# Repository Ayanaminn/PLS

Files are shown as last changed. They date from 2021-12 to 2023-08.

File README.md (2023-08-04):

# PLS (Zebrafish Embryo Photomotor Response and Larval Predator response system)
PLS (Zebrafish Embryo Photomotor Response and Larval Predator response system) is developed for rapid analysis of large cohorts of specimens in PMR and SPR neurotoxicity bioassays. 

PLS includes applications of custom embryo arrays in conjunction with an open-source and inexpensive infrared video imaging system coupled with a dedicated bioinformatic approach that facilitates high-throughput analysis of behavioural phenotypes.

PLS_overview

The photic stimulus is controlled by PMR Control Panel, a custom software application that enables programmable photic stimulus control through interfacing with Arduino-based microcontroller.



**Please cite our manuscript:**

Henry, J., Bai, Y., Kreuder, F., Mawdsley, D., Kaslin, J., & Wlodkowic, D. (2022). Accelerating Chemobehavioral Phenotypic Screening in Neurotoxicology Using a Living Embryo Array System. Zebrafish, 19(1), 32-35. https://doi.org/10.1089/zeb.2021.0072 

Installation:
------------
### Requirements

* Windows operating system.

* [Key Componect List](https://github.com/Ayanaminn/PLS/blob/master/Hardware/Assembley%20Instructions%20and%20Component%20List.docx).

### Software

1. Download the latest release from [Releases](https://github.com/Ayanaminn/PLS/releases).

2. Unzip file and open "PMR control panel" folder.

3. Double click to run "PMR control panel.exe".

### Hardware

1. Following the [Assembly instructions](https://github.com/Ayanaminn/PLS/blob/master/Hardware/Assembley%20Instructions%20and%20Component%20List.docx).

2. Download the latest release from [Releases](https://github.com/Ayanaminn/PLS/releases).

3. Unzip file and open "PMR control panel Arduino script" folder.

4. Using [Arduino IDE](https://www.arduino.cc/en/software) to open the "PMR_control_panel_Arduino_script.ino" and upload it to board.

5. Wire LED circuit to Arduino pin 9 (default pin), if user prefer to use other pins, change pin number in the script accordingly and re-upload.

Getting Started:
------------

1. Connect the Arduino with the computer.

2. In the PMR control panel, select the Arduino port, then click "Connect".

3. Use manual or auto mode to control light stimulus.

4. Disconnect the Arduino before exit the program.

License:
------------

MIT License. See [LICENSE](https://github.com/Ayanaminn/PLS/blob/master/LICENSE) for details.

Contact:
------------

Should you have any questions about this application, please report an issue [here](https://github.com/Ayanaminn/PLS/issues), or send an [email](mailto:yutao.bai@hotmail.com).

If you have further interests about the research this program has been applied for, please [visit our website](https://neurotoxlab.com).

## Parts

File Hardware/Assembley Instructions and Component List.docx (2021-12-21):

Key Component List

- 1x Arduino board. Arduino Uno was validated, however any USB interfacing board that has digital I/O pins with PWM should work.
- 1x BD135 transistor.
- 2x 12V CREE LEDs (High intensity to stimulate PMR).
- 1x Power pack for CREE LEDs (AA-0594), input 9-30V, output 700mA.
- 12x 3 strip flexible 12V adhesive white LEDs (ZD0577) for LPR stimulus lighting (36 total LEDs).
- 1x ZS-X4B Hardwired PWM, with 3-15V circuit soldered to allow to run on 12V.
- 1x flexible 12V adhesive IR (850nm) LEDs (LM3528-WN60) for orthogonal IR lighting (24 total LEDs).
- 1x Micro camera stand for CREE LEDs.
- 1x Standard 12V power supply.
- 1x Laser cut PMMA construction base as per below assembly instructions.

Assembly instructions

1. Laser cut all PMMA components. The design for all components that were laser cut are included as .dxf files. These files are already scaled and should be usable by any laser cutter. Always ensure the laser cutter control program correctly imports the layout and the colour should be changed depending on specific cutting settings for thickness of PMMA. Ensure standard safe operating procedure of the laser cutter.
2. Edge components for the base construction need to be layered and thermally bonded as follows, from inside to out, 2x 1.5mm long, 4.5mm long, 4.5mm outer long and 2x 1.5mm short, 4.5mm short, 4.5mm outer short. The thermal bonding method is described in the supplementary.
3. Once these are bonded every piece will slot together with the base to form the overall construction – this can then be chemically bonded.
4. Included in the .dxf files are the custom plate designs. These are simple two layer thermally bonded constructions, the top layer with the holes and the bottom layer with a standard rectangle.
5. Included in the .dxf files are CREE LED brackets for connection to the micro stand, these will have to be altered depending on the stand.
6. The orthogonal IR LEDs can be adhered to the upper edge (4.5mm outer PMMA layer) of the base construction, ensuring the centre of the LEDs align with the centre of the embryo plate when located.
7. The 12 LPR 3 strip LED sections can be wired together and adhered to the baseplate of the base construction, ensure the wiring exits via one of the allocated holes in the edge design.
8. The orthogonal IR LEDs are to be wired into the hardwired PWM (to allow dimming in the background lighting) and the PWM connected to the 12V power supply.
9. The Arduino Uno should be wired to provide a 3.3V control signal to the BD135 transistor (acts as a switch). The BD 135 transistor is connected in a standard simple transistor circuit with the 12V supply that can be wired with removable connections to either the above CREE LEDs (for PMR) or the below white strip LEDs (for LPR).

For further assistance, information or collaboration please contact the Neurotox Lab (https://www.neurotoxlab.com/) at RMIT.

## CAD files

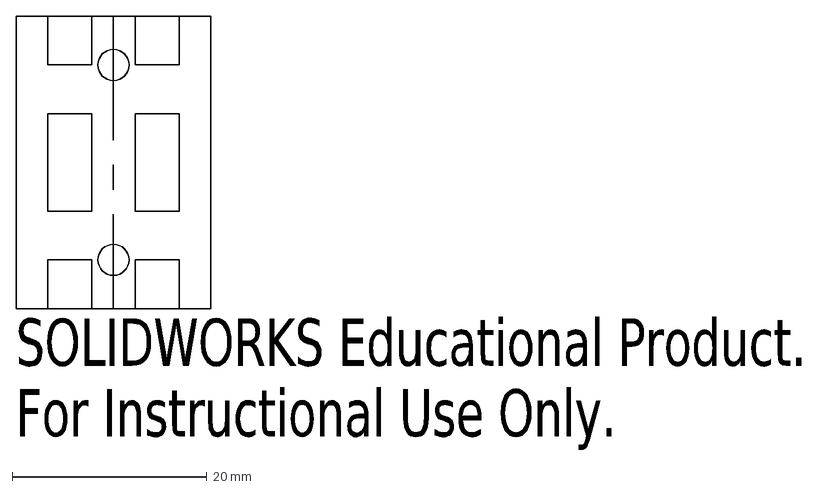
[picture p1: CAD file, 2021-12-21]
Hardware/CREE LED bracket/uprightback_2.DXF
SOLIDWORKS Educational Product.
For Instructional Use Only.

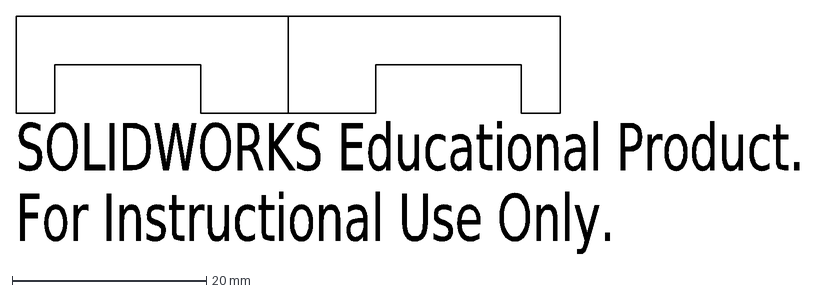
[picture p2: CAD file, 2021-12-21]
Hardware/Main/15short.DXF
SOLIDWORKS Educational Product.
For Instructional Use Only.

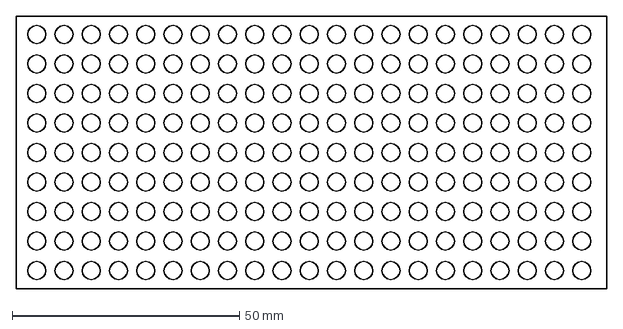
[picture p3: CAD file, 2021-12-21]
Hardware/Plates/zfchip_pmr_plate.DXF
130.0 x 60.0 mm

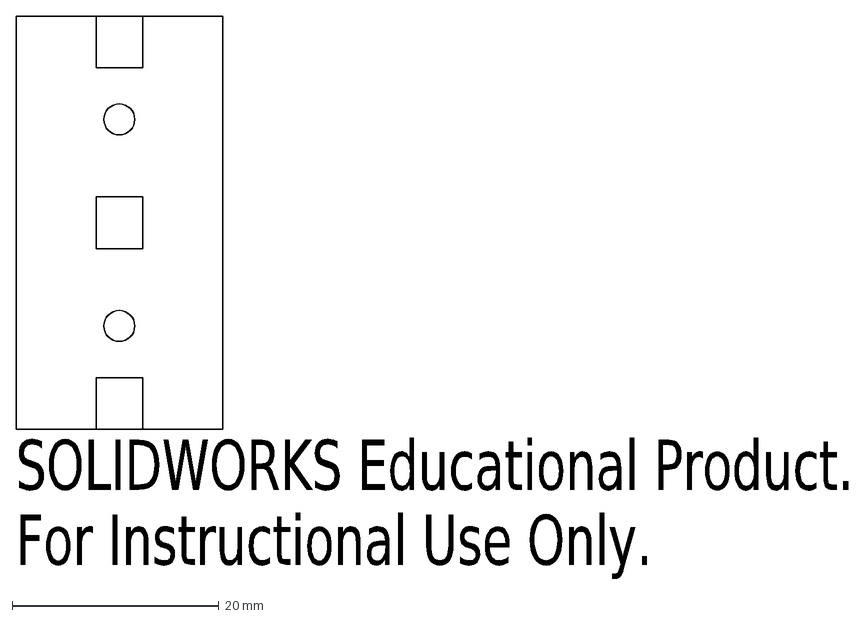
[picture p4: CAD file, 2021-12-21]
Hardware/CREE LED bracket/mountconnection.DXF
SOLIDWORKS Educational Product.
For Instructional Use Only.

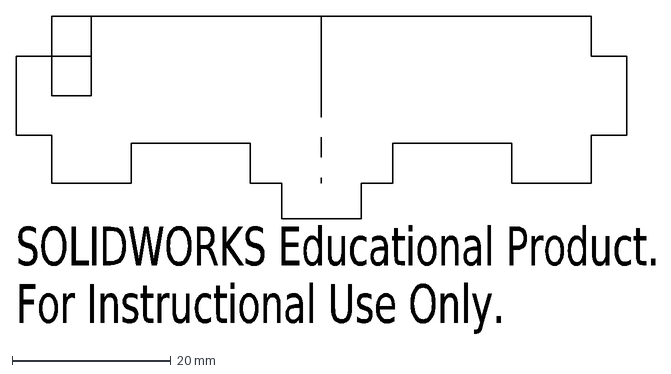
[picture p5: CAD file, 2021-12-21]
Hardware/Main/45outershort.DXF
SOLIDWORKS Educational Product.
For Instructional Use Only.

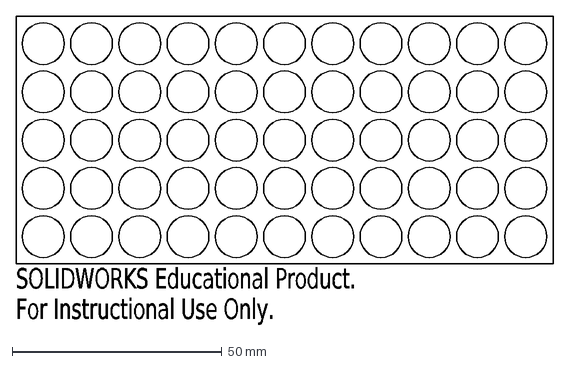
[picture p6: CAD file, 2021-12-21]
Hardware/Plates/zfchip_10mm.DXF
SOLIDWORKS Educational Product.
For Instructional Use Only.

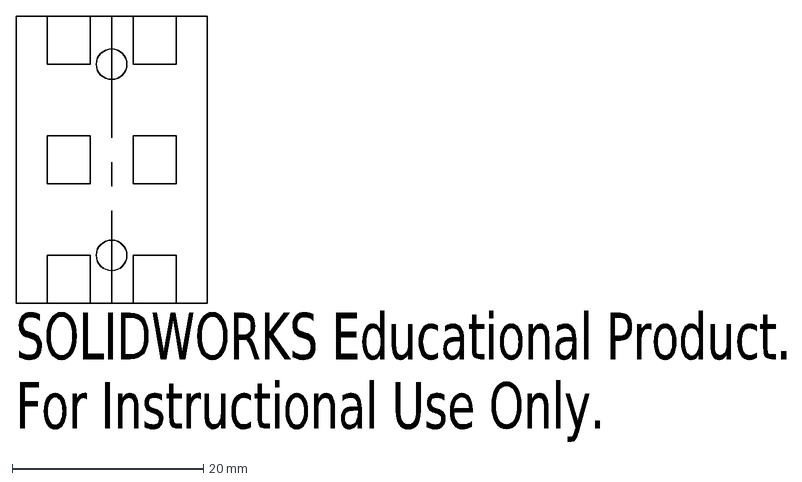
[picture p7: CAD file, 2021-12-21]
Hardware/CREE LED bracket/uprightback.DXF
SOLIDWORKS Educational Product.
For Instructional Use Only.

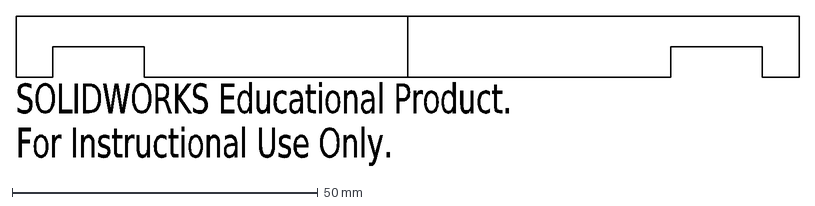
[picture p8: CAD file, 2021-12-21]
Hardware/Main/15long.DXF
SOLIDWORKS Educational Product.
For Instructional Use Only.

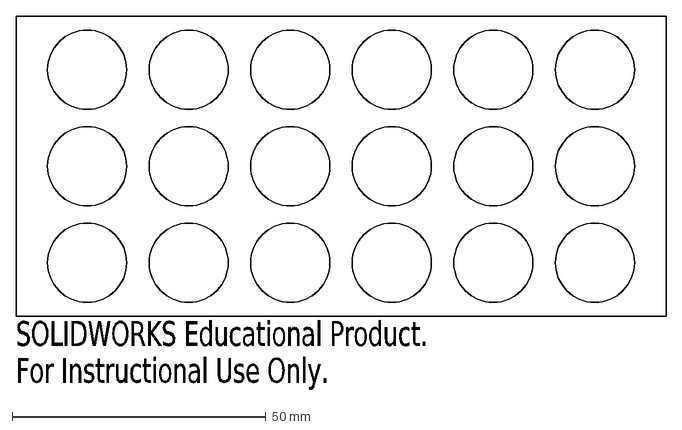
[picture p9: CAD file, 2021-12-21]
Hardware/Plates/zfchip_15dot6mm.DXF
SOLIDWORKS Educational Product.
For Instructional Use Only.

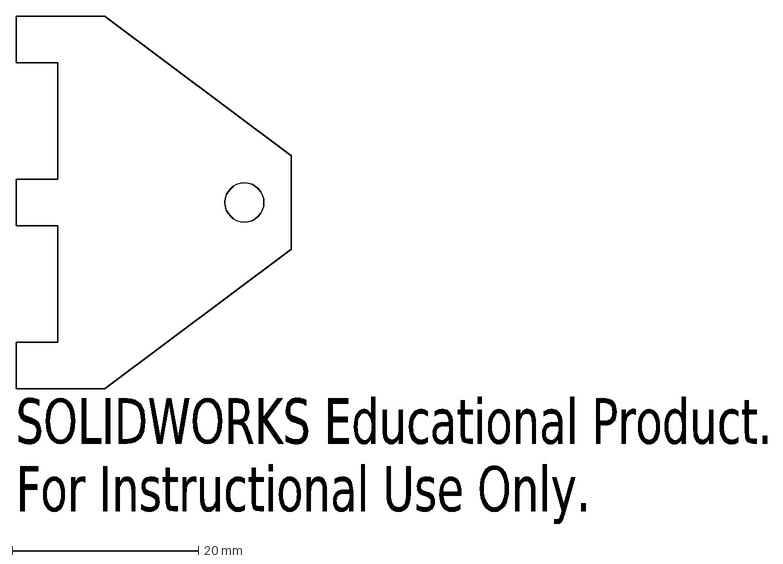
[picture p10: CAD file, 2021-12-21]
Hardware/CREE LED bracket/mountconnecttriangle.DXF
SOLIDWORKS Educational Product.
For Instructional Use Only.

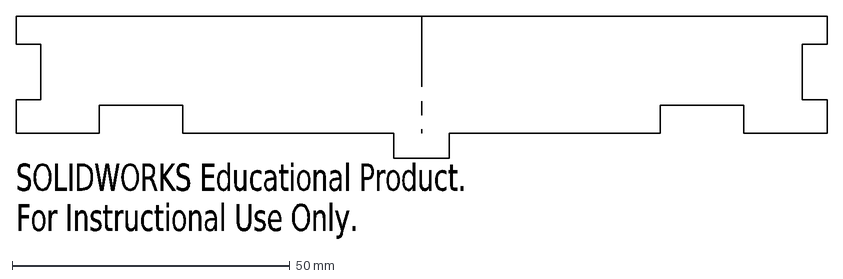
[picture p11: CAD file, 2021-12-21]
Hardware/Main/45outerlong.DXF
SOLIDWORKS Educational Product.
For Instructional Use Only.

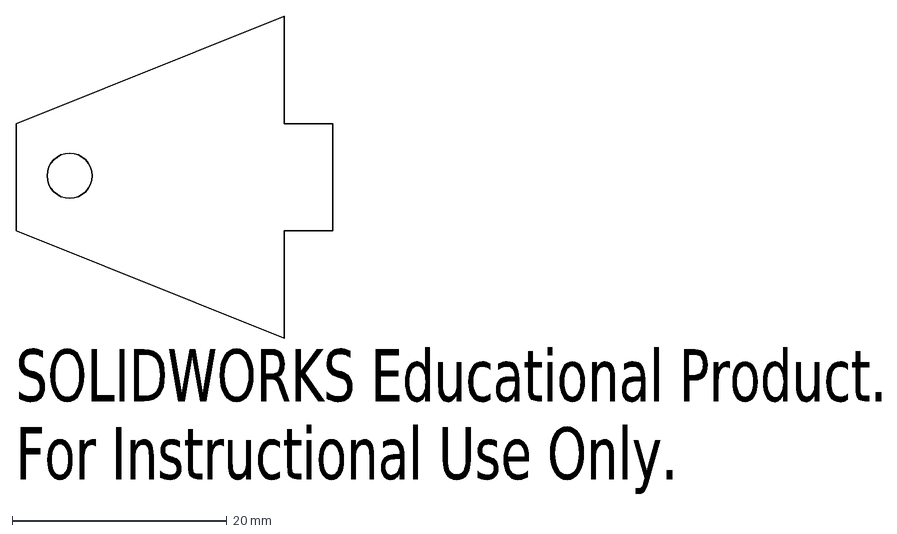
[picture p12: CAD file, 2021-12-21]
Hardware/CREE LED bracket/uprightri_2.DXF
SOLIDWORKS Educational Product.
For Instructional Use Only.

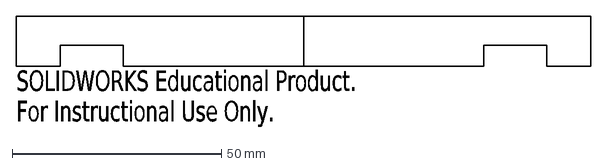
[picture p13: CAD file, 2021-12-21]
Hardware/Main/45long.DXF
SOLIDWORKS Educational Product.
For Instructional Use Only.

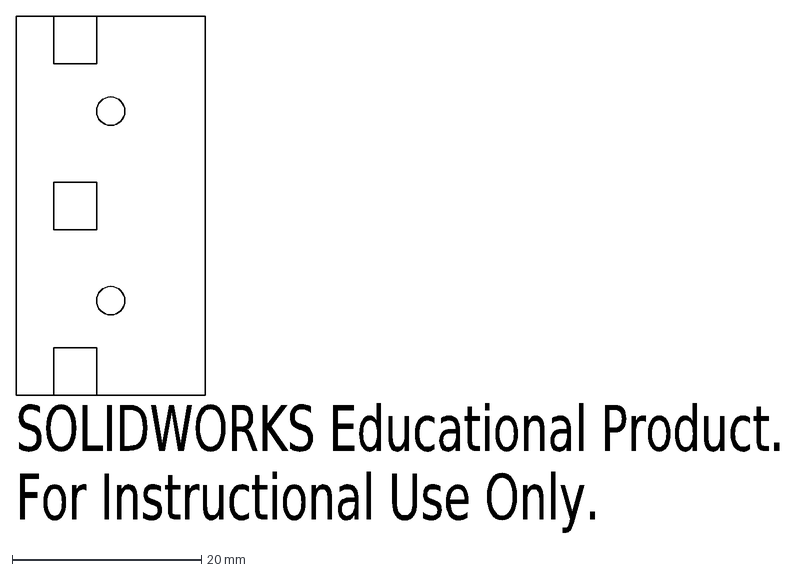
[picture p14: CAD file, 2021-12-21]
Hardware/CREE LED bracket/mountconnection_2.DXF
SOLIDWORKS Educational Product.
For Instructional Use Only.

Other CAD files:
Hardware/Main/base.DXF
Hardware/CREE LED bracket/uprightri.DXF
Hardware/Main/45short.DXF
Hardware/CREE LED bracket/uprightri_3.DXF
Hardware/CREE LED bracket/base.DXF

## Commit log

2021-10-15 Update Arduino script
2021-12-21 add hardware component, update file directory
    [15long.DXF, 15short.DXF, 45long.DXF, 45outerlong.DXF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]
